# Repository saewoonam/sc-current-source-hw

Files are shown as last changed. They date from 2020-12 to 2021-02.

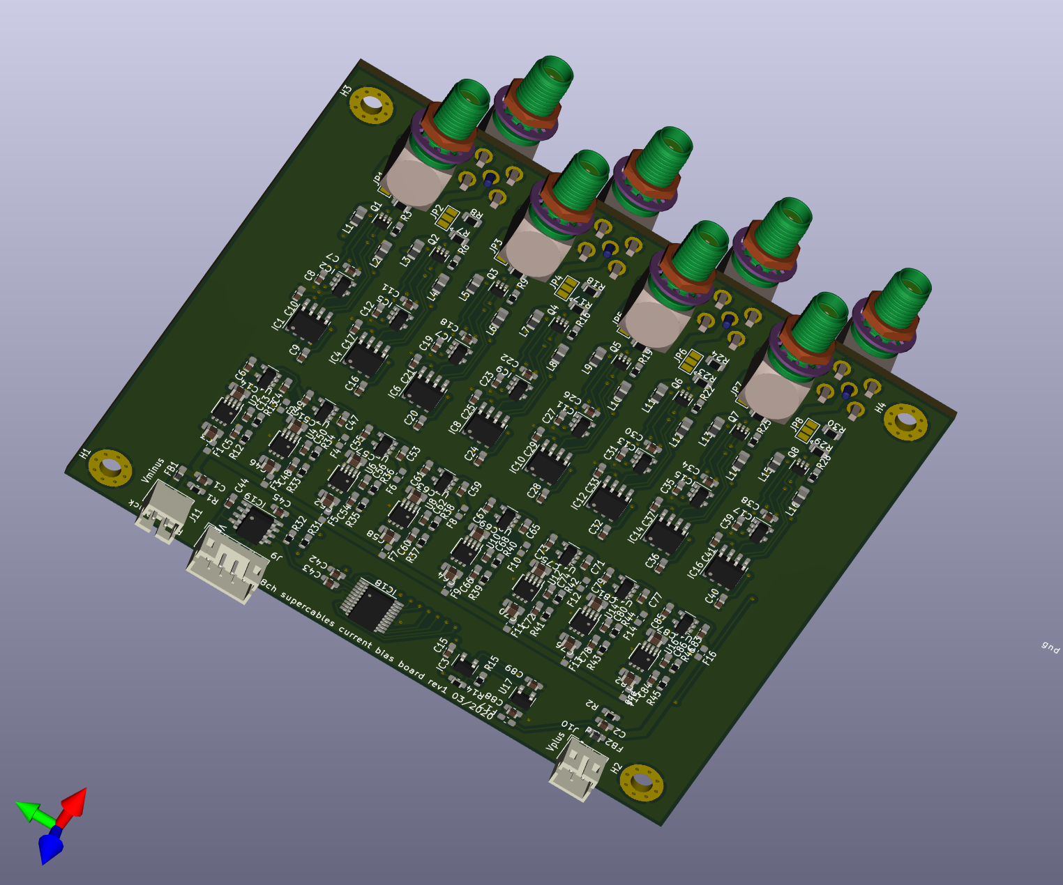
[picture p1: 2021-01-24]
8ch_v5_nosma/8ch_v5_nosma.png

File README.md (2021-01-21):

# CAD file for supercables 8 channel current source

## Folder descriptions:
- 8ch_currentsource_jlc_v4:   KiCAD files of the elecronic circuit
- front_panel:  PCB design for the front panel of the enclosure
- back_panel:  PCB design for rthe back panel of the enclosure
- supercables-curernt-source-enclosure:  FreeCAD file and step files of the assembled box

## [Assembly Instructions](https://github.com/saewoonam/sc-current-source-hw/blob/main/Assembly_Instructions.md)

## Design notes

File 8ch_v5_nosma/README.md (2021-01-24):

# 8ch_currentsource_jlc_v3
Second attempt to make an 8 channel current bias board.  
#  Change from v2
- Added a voltage regulator for each channel

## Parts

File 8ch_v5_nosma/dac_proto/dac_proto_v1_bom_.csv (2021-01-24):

References | Value | Footprint | SPN | SPR
C2 C4 C5 C8 | 0.1uF 50V X7R 0603 | C_0603_1608Metric_Pad1.05x0.95mm_HandSolder | C14663 | LCSC
C6 C7 C9 | 1.0uF 25V X7R 0603 | C_0603_1608Metric_Pad1.05x0.95mm_HandSolder | C29936 | LCSC
C1 C3 | NFM21PS106B0J3D | NFM21PS106B0J3D_v2 | C118986 | LCSC
FB1 | MPZ2012S102AT000 | 805 | C76817 | LCSC
IC1 | AD5675RBRUZ | TSSOP-20_4.4x6.5mm_P0.65mm
IC2 | ISO1541DR | SOIC-8_3.9x4.9mm_P1.27mm | C143028 | LCSC
J1 | Conn_01x04_MountingPin | JST_PH_S4B-PH-SM4-TB_1x04-1MP_P2.00mm_Horizontal
J2 | Conn_01x10_Male | PinHeader_1x10_P2.54mm_Vertical | C89120 | LCSC
J3 | Phoenix 1711725 | TerminalBlock_Phoenix_MKDS-3-2-5.08_1x02_P5.08mm_Horizontal | - | -
JP1 JP2 JP3 JP4 | SolderJumper_2_Open | SolderJumper-2_P1.3mm_Open_RoundedPad1.0x1.5mm
R1 | 2 | R_0603_1608Metric_Pad1.05x0.95mm_HandSolder | C22977 | LCSC
U1 | LP5907MFX-3.3 | SOT-23-5 | C80670 | LCSC

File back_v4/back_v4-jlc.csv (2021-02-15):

Comment | Designator | MPN | LCSC
BAT60B | D1, | BAT60B | C514095
LED | D2, | KT-0603R | C2286
MountingHole | H1,
JST-PH2 | J1, | B2B-PH-SM4-TB(lf)(sn)
JST-SH | J2, J5, | JST-SH-BM04B-SRSS-TB
191-009-113L551 | J3, | 191-009-113L551
STEMMA JST-PH connector | J4, | B4B-PH-SM4-TB(lf)(sn)
10K | R1, R2, | 0603WAF1002T5E | C25804
2K | R3, | 0603WAF2001T5E | C22975
3.3K | R4, | 0603WAF3301T5E | C22978
1K | R5, | 0603WAF1001T5E | C21190
QT_PY | U1, | -
AQY212 | U2, | AQY212GSZ | C129283

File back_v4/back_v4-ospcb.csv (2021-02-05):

Designator | MPN | Quantity | Description
D1, | BAT60AE6327 | 1 | BAT60A
H1, |  | 1 | MountingHole
J1, | B2B-PH-SM4-TB(lf)(sn) | 1 | JST-PH2
J2, J5, | JST-SH-BM04B-SRSS-TB | 2 | JST-SH
J3, | 191-009-113L551 | 1 | 191-009-113L551
J4, | B4B-PH-SM4-TB(lf)(sn) | 1 | STEMMA JST-PH connector
R1, R2, | 0603WAF1002T5E | 2 | 10K
R3, R5, | 0603WAF2001T5E | 2 | 2K
R4, | 0603WAF3301T5E | 1 | 3.3K
U1, | - | 1 | QT_PY
U2, | AQY212GSZ | 1 | AQY212

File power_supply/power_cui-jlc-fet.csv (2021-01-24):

Comment | Designator | MPN | LCSC
4.7uF | C1, | CL32B475KBUYNNE | C29823
10uF | C2, C3, C8, | EMK325B7106KN-T | C13585
330uF 35V | C4, | VE-331M1VTR-1010S | C134522
CP | C5, C6, | DB-5R5D155T
100uF | C7, | CL32A107MQVNNNE | C49066
390pF | C9, C10, |  | C84719
BAT60A | D1, D2, D3, D4, D5, D6, D7, | BAT60AE6327 | C117485
JK-NSMD050-13.2V | F1, | JK-NSMD050-13.2V | C369159
ACM9070-701-2PL-TL01 | FL1, FL2, | ACM9070-701-2PL-TL01 | C14594
Bnx029-01 | FL4, FL5, | Bnx029-01L | C124739
Barrel_Jack_Switch | J1, | PJ-066A
Conn_01x02 | J2, J3, J4, J5, J6, J7, | B2B-PH-K-S(LF)(SN)
SolderJumper_2_Open | JP1, JP2, JP3, JP4, | -
4.7uH | L1, | SDET25201T-4R7MS | C520141
22uH | L2, |  | C207843
NUD3105LT1G | Q1, Q2, | NUD3105LT1G | C14894
BSS84 | Q3, |  | C8492
ZVN4525G | Q4, |  | C154905
ZXP2106G | Q5, |  | C460270
10K | R1, R3, R7, | 0603WAF1002T5E | C25804
1K | R2, R6, | 0603WAF1001T5E | C21190
750 | R4, R5, | 0603WAF7500T5E | C23241
S20K30 | RV1, | S20K30
PDQE10-Q24-D5-D | U1, | PDQE10-Q24-D5-D
AQY212GSZ | U2, U3, | AQY212GSZ | C129283
CRE1S1205SC | U4,

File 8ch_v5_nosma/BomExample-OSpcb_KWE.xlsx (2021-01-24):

Designator | MPN | Qty | Description
C1, C2, C4, C6, C47, C49, C53, C55, C59, C61, C65, C67, C71, C73, C77, C79, C83, C85, C88, C89, | CL10B105KA8NNNC | 20 | 1uF
C3, C14, C46, C51, C52, C57, C58, C63, C64, C69, C70, C75, C76, C81, C82, C87, | CL31B106KBHNNNE | 16 | 10uF X5R 0805
C5, C13, C48, C50, C54, C56, C60, C62, C66, C68, C72, C74, C78, C80, C84, C86, | 0603B103K500NT | 16 | 10nF 50V X7R 0603
C7, C8, C9, C10, C11, C12, C15, C16, C17, C18, C19, C20, C21, C22, C23, C24, C25, C26, C27, C28, C29, C30, C31, C32, C33, C34, C35, C36, C37, C38, C39, C40, C41, C42, C43, C44, C45, | CC0603KPX7R7BB104 | 37 | 100nF
F1, F2, F3, F4, F5, F6, F7, F8, F9, F10, F11, F12, F13, F14, F15, F16, F17, | TLC-FSMD020 | 17 | Polyfuse
FB1, FB2, | BLM18PG181SN1D | 2 | BLM18PG181SN1D
H1, H2, H3, H4, | DNI | 4 | MountingHole_Pad
IC1, IC4, IC6, IC8, IC10, IC12, IC14, IC16, | AD8276ARMZ | 8 | AD8276
IC2, IC3, IC5, IC7, IC9, IC11, IC13, IC15, IC17, | OPA376AIDBVR | 9 | OPA376xxDBVR
IC18, | AD5675RBRUZ | 1 | AD5675RBRUZ
IC19, | ISO1541DR | 1 | ISO1541DR
J1, J2, J3, J4, J5, J6, J7, J8, | SMA-KWE20 | 8 | Conn_Coaxial
J9, | B4B-PH-K-S(LF)(SN) | 1 | B4B-PH-K
J10, J11, | B2B-PH-K-S(LF)(SN) | 2 | JST B2B-PH-K
JP1, JP2, JP3, JP4, JP5, JP6, JP7, JP8, | DNI | 8 | SolderJumper_3_Open
L1, L2, L3, L4, L5, L6, L7, L8, L9, L10, L11, L12, L13, L14, L15, L16, | MMZ2012Y152BTD25 | 16 | MMZ2012Y152B
Q1, Q2, Q3, Q4, Q5, Q6, Q7, Q8, | MMDT3946-7-F | 8 | MMDT3946-7-F
R1, R2, | RC0603FR-072RL | 2 | 2
R3, R6, R9, R14, R15, R16, R19, R22, R25, R28, | RC0603FR-071KL | 10 | 1k
R4, R7, R10, R17, R20, R23, R26, R29, | 2-1625868-7 | 8 | 10 0.1%
R5, R8, R11, R18, R21, R24, R27, R30, | ERA-6AEB102V | 8 | 1k 0.1%
R12, R33, R35, R37, R39, R41, R43, R45, | 0603WAF2002T5E | 8 | 20K
R13, R34, R36, R38, R40, R42, R44, R46, | 0603WAF3572T5E | 8 | 35.7K
R31, R32, | 0603WAF1002T5E | 2 | 10K
U1, U3, U5, U7, U9, U11, U13, U15, U17, | LP5907MFX-3.3 | 9 | LP5907MFX-3.3
U2, U4, U6, U8, U10, U12, U14, U16, | TPS7A3001DGNR | 8 | TPS7A3001

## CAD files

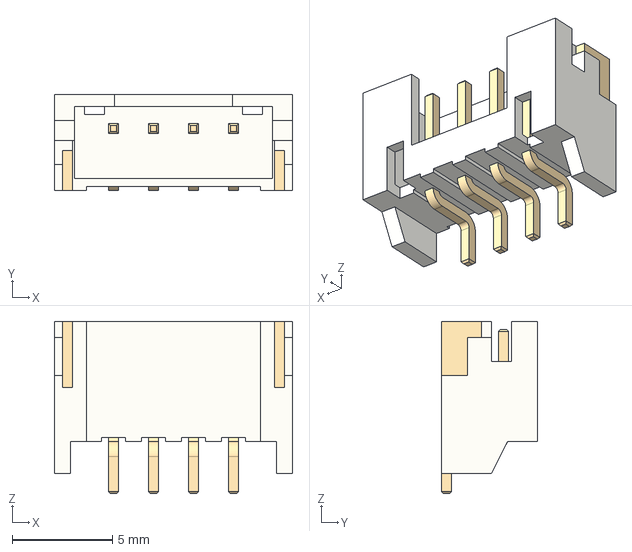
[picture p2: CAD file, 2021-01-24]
8ch_v5_nosma/3D/S4B-PH-SM4-TB.stp
11.9 x 4.80 x 8.60 mm

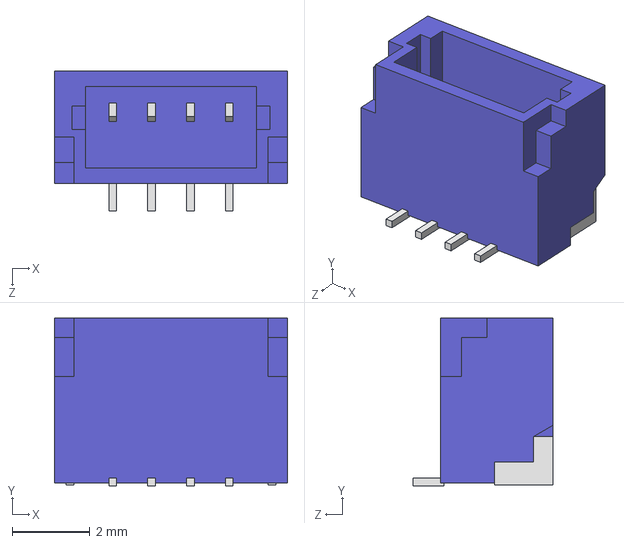
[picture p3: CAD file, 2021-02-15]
back_v4/3D/BM04B-SRSS-TB.STEP
6.00 x 4.32 x 3.60 mm

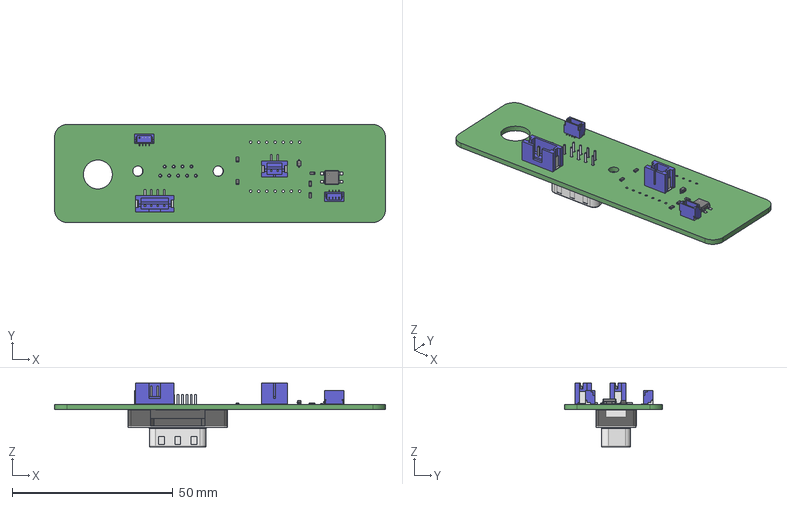
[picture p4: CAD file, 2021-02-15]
back_v4/back_v4.step
103.0 x 30.5 x 19.9 mm

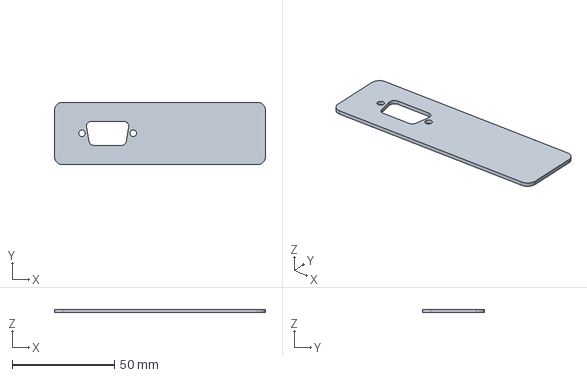
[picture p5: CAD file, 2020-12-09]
front_panel/back_panel.step
103.0 x 30.5 x 1.60 mm

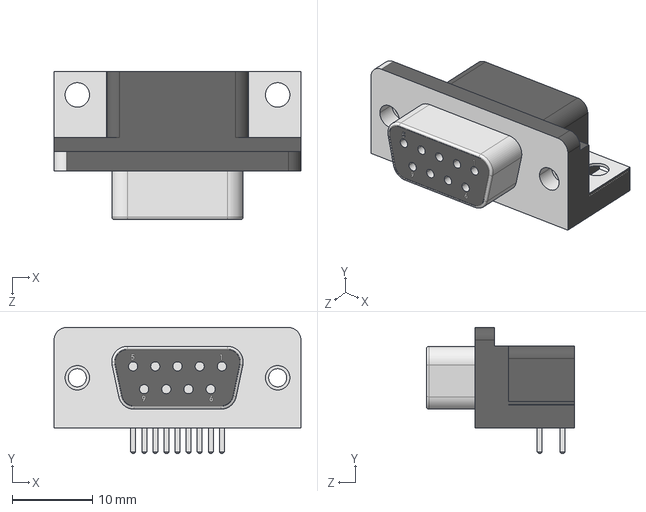
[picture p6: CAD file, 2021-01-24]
power_supply/3D/182-009-213.STEP
30.8 x 15.7 x 18.5 mm

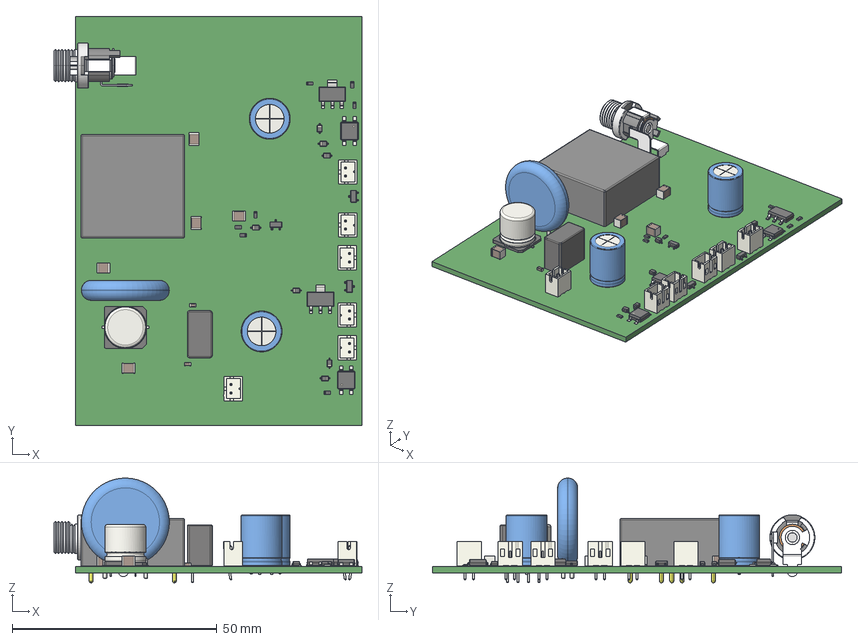
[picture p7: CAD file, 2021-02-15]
power_supply/power_cui.step
75.2 x 100.0 x 25.6 mm

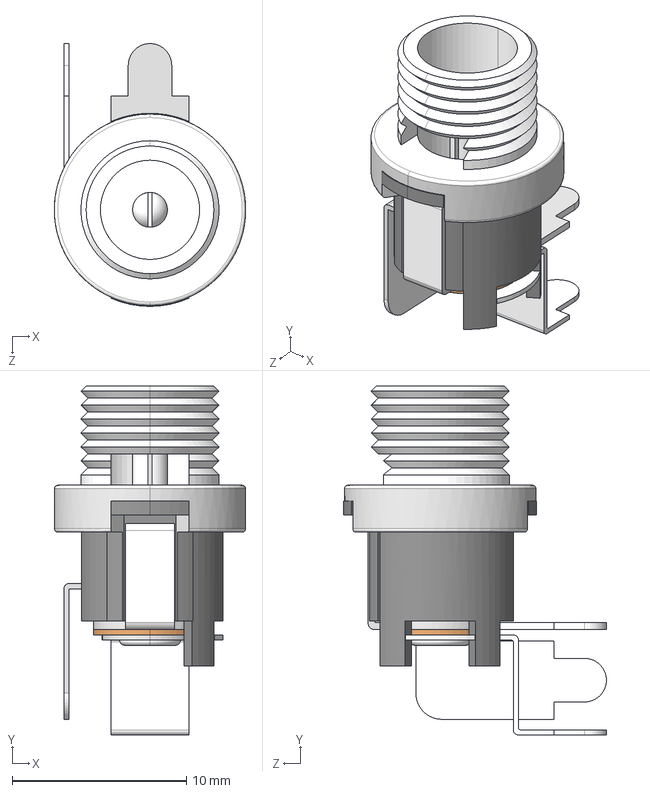
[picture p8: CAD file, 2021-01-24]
supercap/3D/CUI_DEVICES_PJ-066A.step
11.0 x 20.1 x 15.1 mm

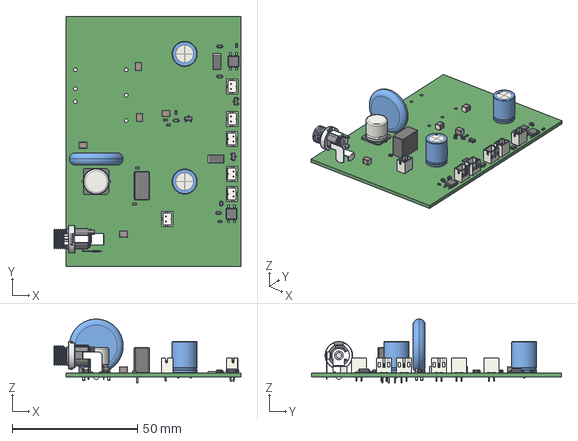
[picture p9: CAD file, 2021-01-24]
supercap/supercap.step
74.7 x 100.0 x 25.5 mm

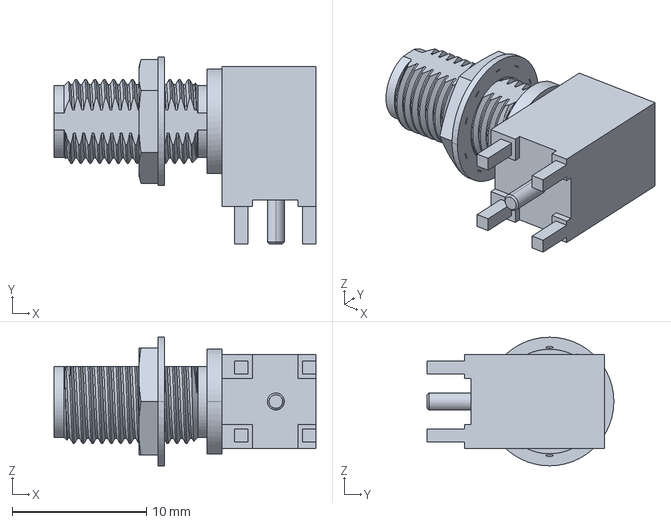
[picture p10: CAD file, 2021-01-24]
8ch_v5_nosma/3D/molex_732512201.stp
19.5 x 13.9 x 9.60 mm

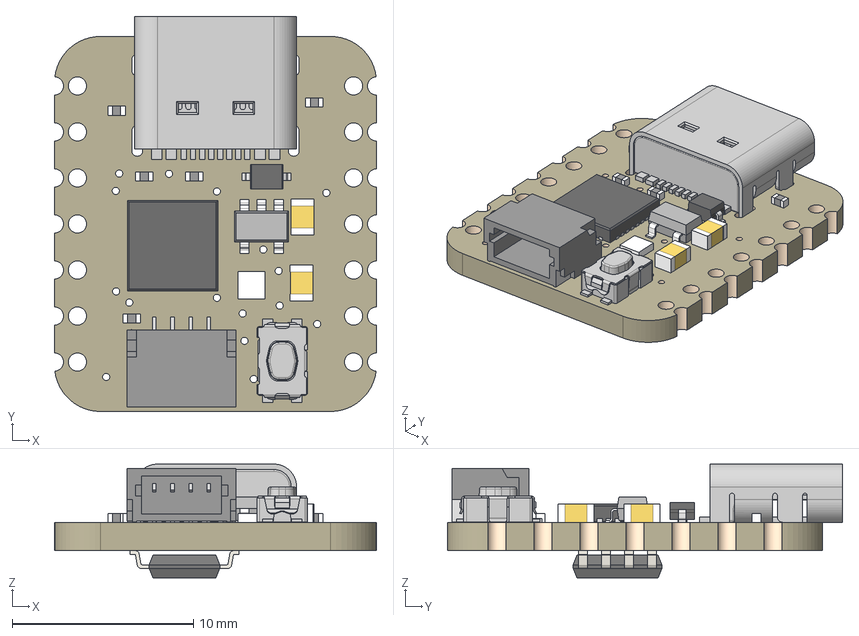
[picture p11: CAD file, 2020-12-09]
back_v4/3D/4600 QTPy.step
17.8 x 21.8 x 6.28 mm
Board
10uF x 2
reset
ATSAMD21E
TPB1,27
5.1K x 5
USB TYPE C
STEMMA_I2C_QTSKINNY
AP2112K-3.3
WS2812B_SK6805_1515
NSR0320
SOIC8_150MIL

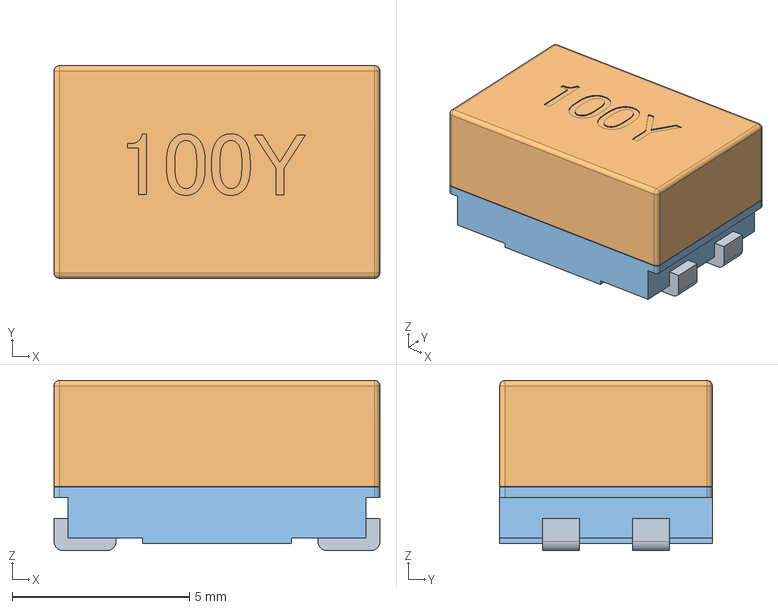
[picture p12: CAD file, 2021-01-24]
power_supply/3D/srf0905-100y.stp
9.20 x 6.00 x 4.80 mm

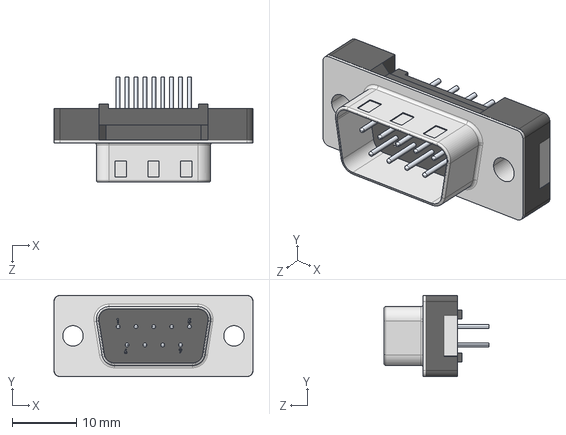
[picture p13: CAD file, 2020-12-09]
back_v4/3D/191-009-113.STEP
30.9 x 12.6 x 16.3 mm

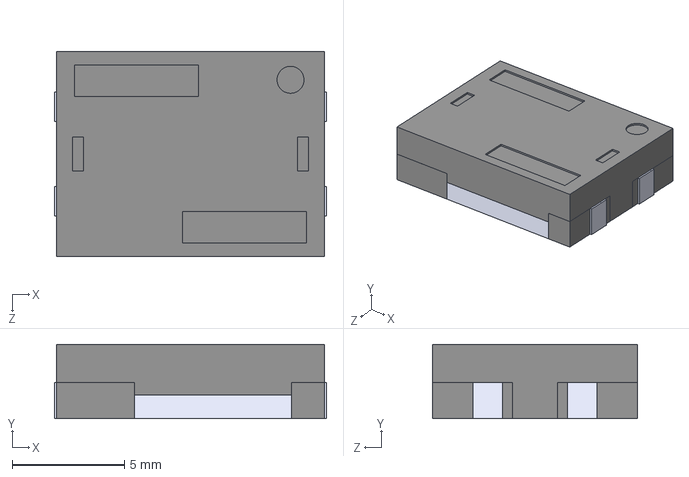
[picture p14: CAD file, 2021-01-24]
power_supply/3D/BNX022-01L.STEP
12.1 x 3.30 x 9.10 mm

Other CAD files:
back_v3/back_v3.step
back_v4/3D/B4B-PH-SM4-TB.STEP

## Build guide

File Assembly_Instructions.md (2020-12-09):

# Ideal assembly instructions
## Parts list for one enclosure
- 8 channel current source circuit board
- front panel PCB with cutouts for SMA connectors
- back panel PCB
- [Hammand 1445L1201 enclosure enclosure](https://www.hawkusa.com/manufacturers/hammond-mfg/enclosures/box-metal/1455l1201?utm_source=octopart&utm_medium=cpc)
- [JST-PH 2 pin power jumper cables](https://www.adafruit.com/product/4714)
- [i2c JST-PH 4 jumper / STEMMA cable](https://www.adafruit.com/product/3568)
- [QT-py adafruit microcontroller](https://www.adafruit.com/product/4600)
- DB9 female pigtail

## Assembly instructions
1.  attach 2 power cable jumpers, one for positive, one for negative voltages to the 8 channel PCB
1.  attach the JST-PH 4 stemma cable to the 8 channel PCB
1.  Remove the metal front and metal back panels from the Hammond enclosure
1.  Slide the printed 8 channel  PCB into hammond enclosure.   Use the middle set of PCB card guides
1.  Attach the front panel PCB to the hammond enclosure.   
1.  Slide the SMA connectors from the 8 channel PCB board through the front panel mounting holes for the SMA connectors.
1.  Use the lock washer and nut to attach each SMA to the front panel PCB
1.  Solder the Adafruit QT PY to the back panel
1.  Connect the power jumper cables and the JST-PH 4 Stemma cable to the back panel
1.  Feed cables into the box and attach back panel to the box
1.  Attach right angle USB-C adapter to the QT-PY board
1.  Attach DB9 pigtail to the backpanel DB9 connector
1.  Apply power to DB9 cable  **Need wirinig details**

## Assembly instructions for backpanel
### Parts list
- 1 Unpopulated back panel PCB
- 2 B2B-PH-SM4-TB  JST-PH 2 pin connector
- 1 B4B-PH-SM4-TB  JST-PH 4 pin connector
- 1 NorComp  191-009-113L551  DB9 male connector
- QT-PY Adafruit microcontroller
### Instructions
1.  Solder JST connectors to one side of the board
2.  Solder DB9 and QT-PY microcontroller to the board on the other side

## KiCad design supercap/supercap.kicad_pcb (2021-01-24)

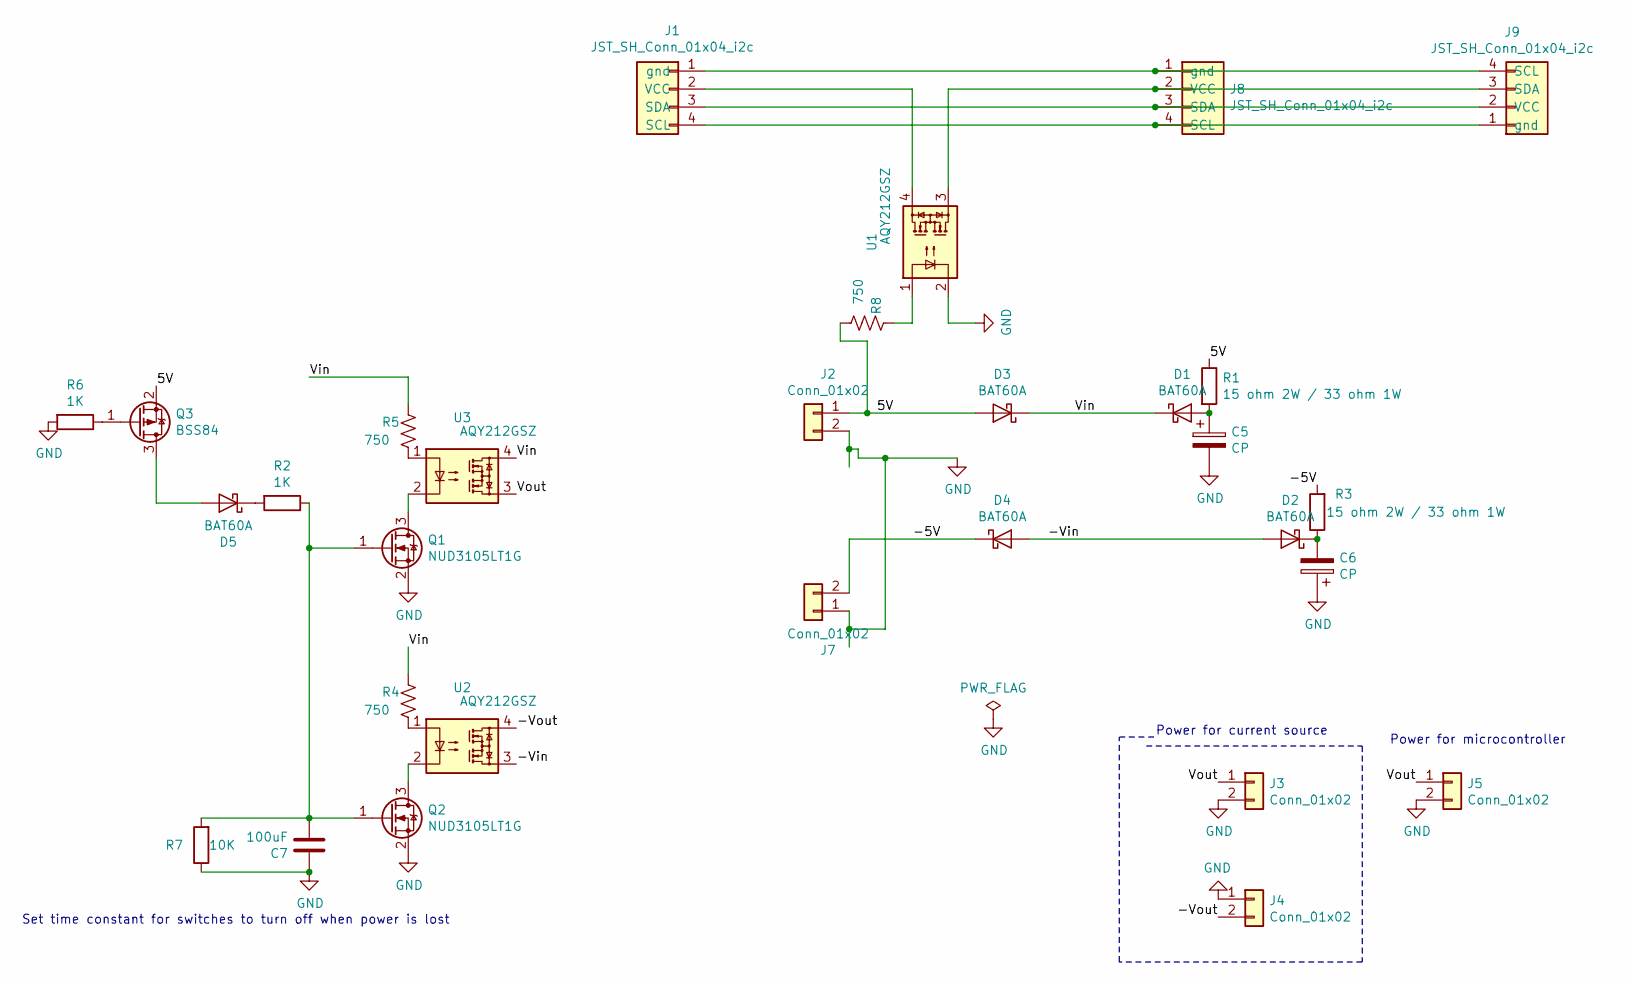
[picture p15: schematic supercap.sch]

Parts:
C5, C6: CP; C_Radial_D21.5mm_H8mm_P5.00mm; MPN DB-5R5D155T
C7: 100uF; C_1210_3225Metric_Pad1.42x2.65mm_HandSolder; MPN CL32A107MQVNNNE; LCSC C49066
D1, D2, D3, D4: BAT60A; D_SOD-323; MPN BAT60AE6327
D5: BAT60A; D_SOD-323; MPN BAT60AE6327; LCSC C117485
J1, J8, J9: JST_SH_Conn_01x04_i2c; JST_SH_BM04B-SRSS-TB_1x04-1MP_P1.00mm_Vertical
J2, J3, J4, J5, J7: Conn_01x02; JST_PH_B2B-PH-K_1x02_P2.00mm_Vertical; MPN B2B-PH-K-S(LF)(SN)
Q1, Q2: NUD3105LT1G; SOT-23; MPN NUD3105LT1G; LCSC C14894
Q3: BSS84; SOT-23; LCSC C8492
R1, R3: 15 ohm 2W / 33 ohm 1W; R_2512_6332Metric_Pad1.52x3.35mm_HandSolder; MPN CRM2512-FX-15R0ELF; LCSC C53728
R2, R6: 1K; R_0603_1608Metric_Pad1.05x0.95mm_HandSolder; MPN 0603WAF1001T5E; LCSC C21190
R4, R5, R8: 750; R_0603_1608Metric_Pad1.05x0.95mm_HandSolder; MPN 0603WAF7500T5E; LCSC C23241
R7: 10K; R_0603_1608Metric_Pad1.05x0.95mm_HandSolder; MPN 0603WAF1002T5E; LCSC C25804
U1, U2, U3: AQY212GSZ; SO-4_4.4x4.3mm_P2.54mm; MPN AQY212GSZ; LCSC C129283

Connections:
/5V: D3.2 (A), J2.1, Q3.2 (S), R1.1, R8.2
/-5V: D4.1 (K), J7.2, R3.2
/-Vin: D2.2 (A), D4.2 (A), U2.3
/-Vout: J4.2, U2.4
/Vin: D1.1 (K), D3.1 (K), R4.1, R5.1, U3.4
/Vout: J3.1, J5.1, U3.3
GND: C5.2, C6.1, C7.1, J2.2, J3.2, J4.1, J5.2, J7.1, Q1.2 (S), Q2.2 (S), R6.2, R7.1, U1.2
unnamed: C5.1, D1.2 (A), R1.2
unnamed: C6.2, D2.1 (K), R3.1
unnamed: C7.2, Q1.1 (G), Q2.1 (G), R2.1, R7.2
unnamed: D5.1 (K), R2.2
unnamed: D5.2 (A), Q3.3 (D)
unnamed: J1.1 (gnd), J8.1 (gnd), J9.4 (SCL)
unnamed: J1.2 (VCC), U1.4
unnamed: J1.3 (SDA), J8.3 (SDA), J9.2 (VCC)
unnamed: J1.4 (SCL), J8.4 (SCL), J9.1 (gnd)
unnamed: J8.2 (VCC), J9.3 (SDA), U1.3
unnamed: Q1.3 (D), U3.2
unnamed: Q2.3 (D), U2.2
unnamed: Q3.1 (G), R6.1
unnamed: R4.2, U2.1
unnamed: R5.2, U3.1
unnamed: R8.1, U1.1

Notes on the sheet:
Power for current source
Power for microcontroller
Set time constant for switches to turn off when power is lost

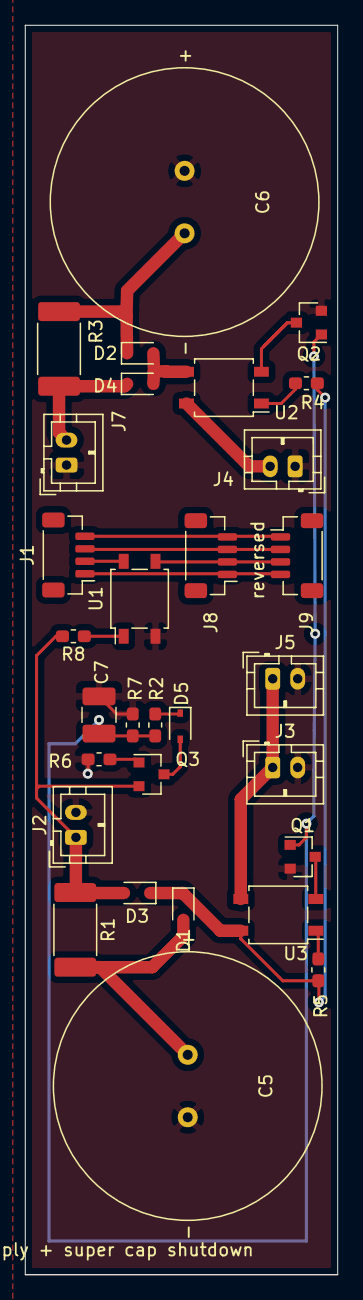
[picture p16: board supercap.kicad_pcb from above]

Board: 2 copper layers, 25.0 x 100.0 mm, 30 parts (0 on the bottom side), 23 nets.

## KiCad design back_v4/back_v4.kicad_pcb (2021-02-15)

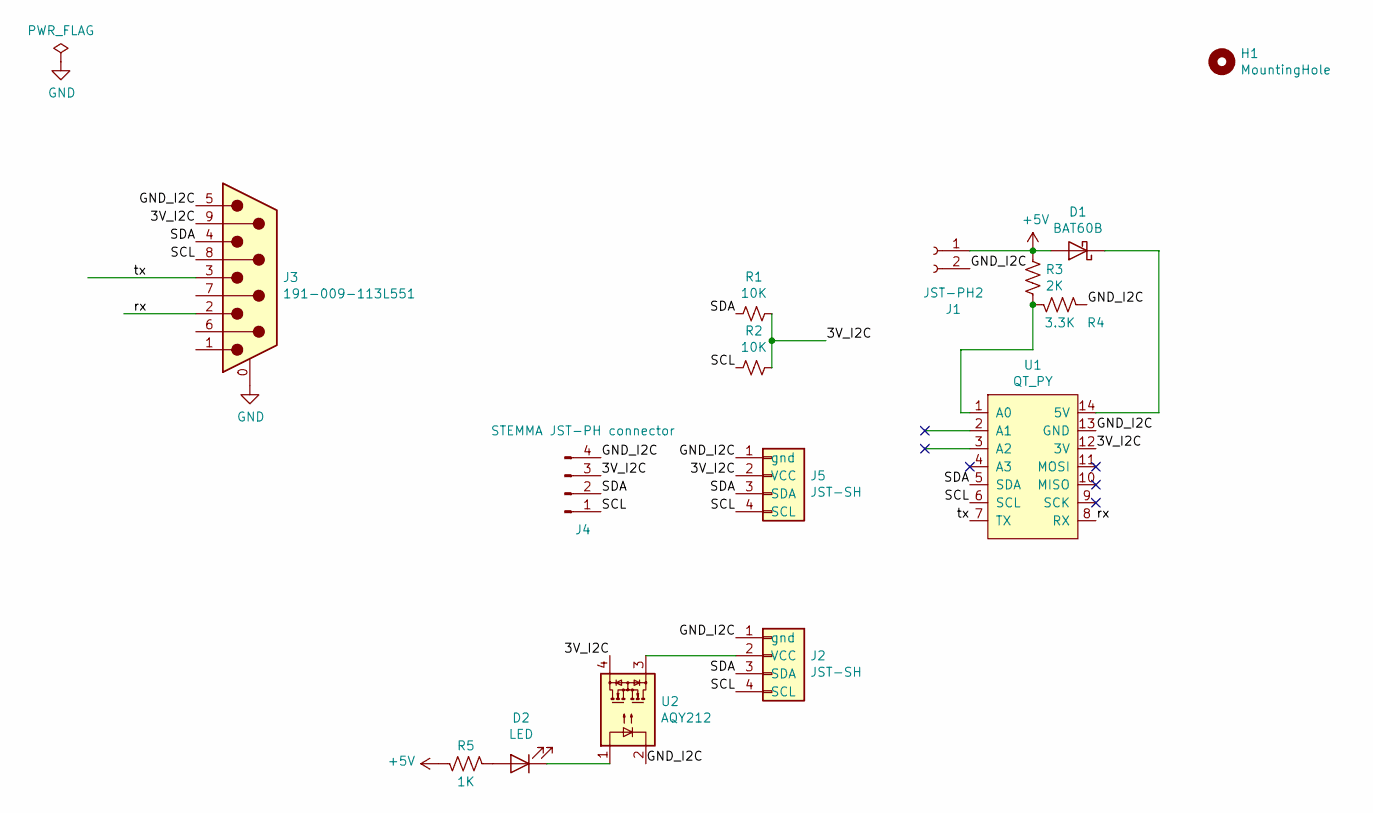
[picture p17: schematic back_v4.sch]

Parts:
D1: BAT60B; D_SOD-323; MPN BAT60B; LCSC C514095
D2: LED; LED_0603_1608Metric_Pad1.05x0.95mm_HandSolder; MPN KT-0603R; LCSC C2286
H1: MountingHole; MountingHole_8.4mm_PJ-066
J1: JST-PH2; JST_PH_B2B-PH-SM4-TB_1x02-1MP_P2.00mm_Vertical; MPN B2B-PH-SM4-TB(lf)(sn)
J2, J5: JST-SH; JST_SH_BM04B-SRSS-TB_1x04-1MP_P1.00mm_Vertical; MPN JST-SH-BM04B-SRSS-TB
J3: 191-009-113L551; DSUB-9_Male_Vertical_P2.77x2.84mm_MountingHoles; MPN 191-009-113L551
J4: STEMMA JST-PH connector; JST_PH_B4B-PH-SM4-TB_1x04-1MP_P2.00mm_Vertical; MPN B4B-PH-SM4-TB(lf)(sn)
R1: 10K; R_0603_1608Metric_Pad1.05x0.95mm_HandSolder; MPN 0603WAF1002T5E
R2: 10K; R_0603_1608Metric_Pad1.05x0.95mm_HandSolder; MPN 0603WAF1002T5E; LCSC C25804
R3: 2K; R_0603_1608Metric_Pad1.05x0.95mm_HandSolder; MPN 0603WAF2001T5E; LCSC C22975
R4: 3.3K; R_0603_1608Metric_Pad1.05x0.95mm_HandSolder; MPN 0603WAF3301T5E; LCSC C22978
R5: 1K; R_0603_1608Metric_Pad1.05x0.95mm_HandSolder; MPN 0603WAF1001T5E; LCSC C21190
U1: QT_PY; QT_PY_DIP-14_600_ELL
U2: AQY212; SO-4_4.4x4.3mm_P2.54mm; MPN AQY212GSZ; LCSC C129283

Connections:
+5V: D1.2 (A), J1.1, R3.1, R5.1
/3V_I2C: J3.9, J4.3, J5.2 (VCC), R1.1, R2.1, U1.12 (3V), U2.4
/GND_I2C: J1.2, J2.1 (gnd), J3.5, J4.4, J5.1 (gnd), R4.2, U1.13 (GND), U2.2
/SCL: J2.4 (SCL), J3.8, J4.1, J5.4 (SCL), R2.2, U1.6 (SCL)
/SDA: J2.3 (SDA), J3.4, J4.2, J5.3 (SDA), R1.2, U1.5 (SDA)
/rx: J3.2, U1.8 (RX)
/tx: J3.3, U1.7 (TX)
GND: J3.0 (PAD)
unnamed: D1.1 (K), U1.14 (5V)
unnamed: D2.1 (K), U2.1
unnamed: D2.2 (A), R5.2
unnamed: J2.2 (VCC), U2.3
unnamed: R3.2, R4.1, U1.1 (A0)

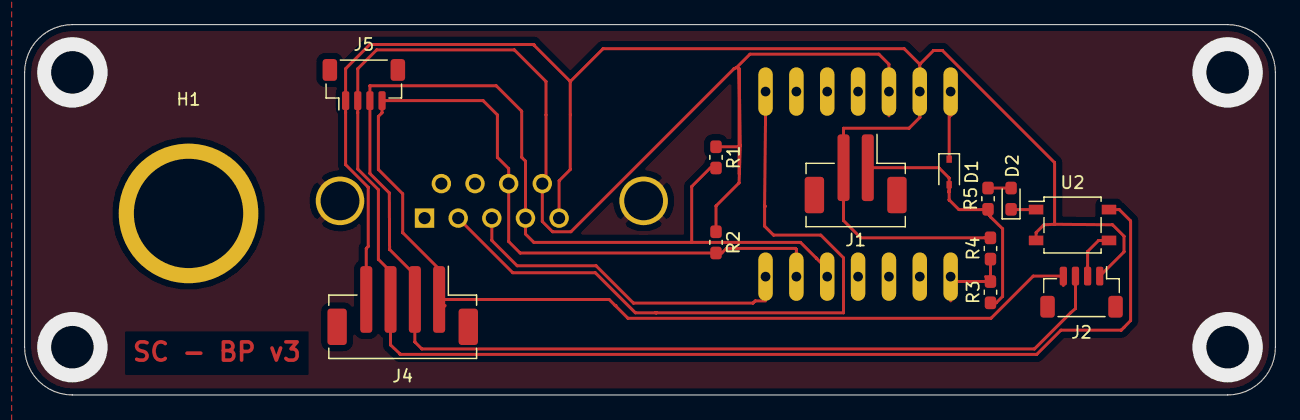
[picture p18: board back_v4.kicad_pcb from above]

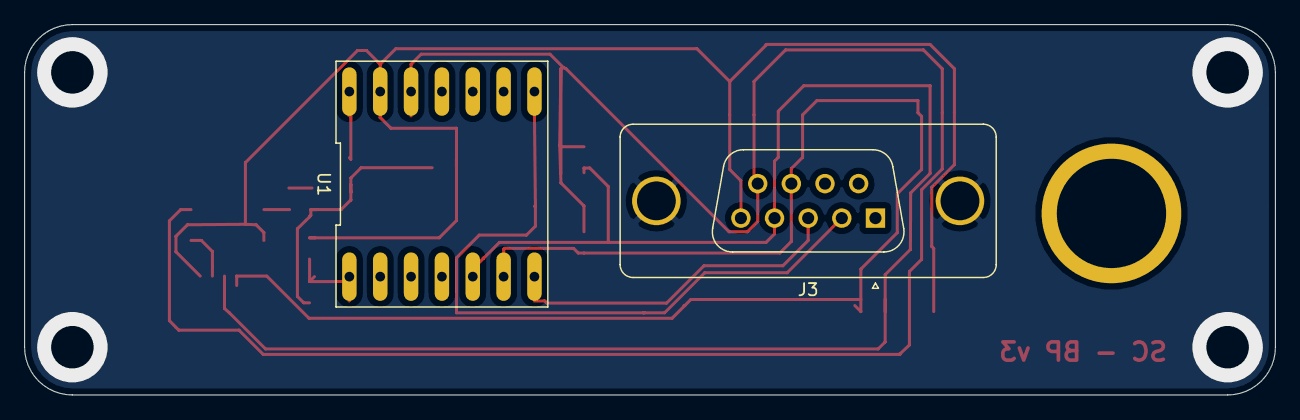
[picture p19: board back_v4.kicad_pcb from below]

Board: 2 copper layers, 103.0 x 30.5 mm, 15 parts (2 on the bottom side), 12 nets.

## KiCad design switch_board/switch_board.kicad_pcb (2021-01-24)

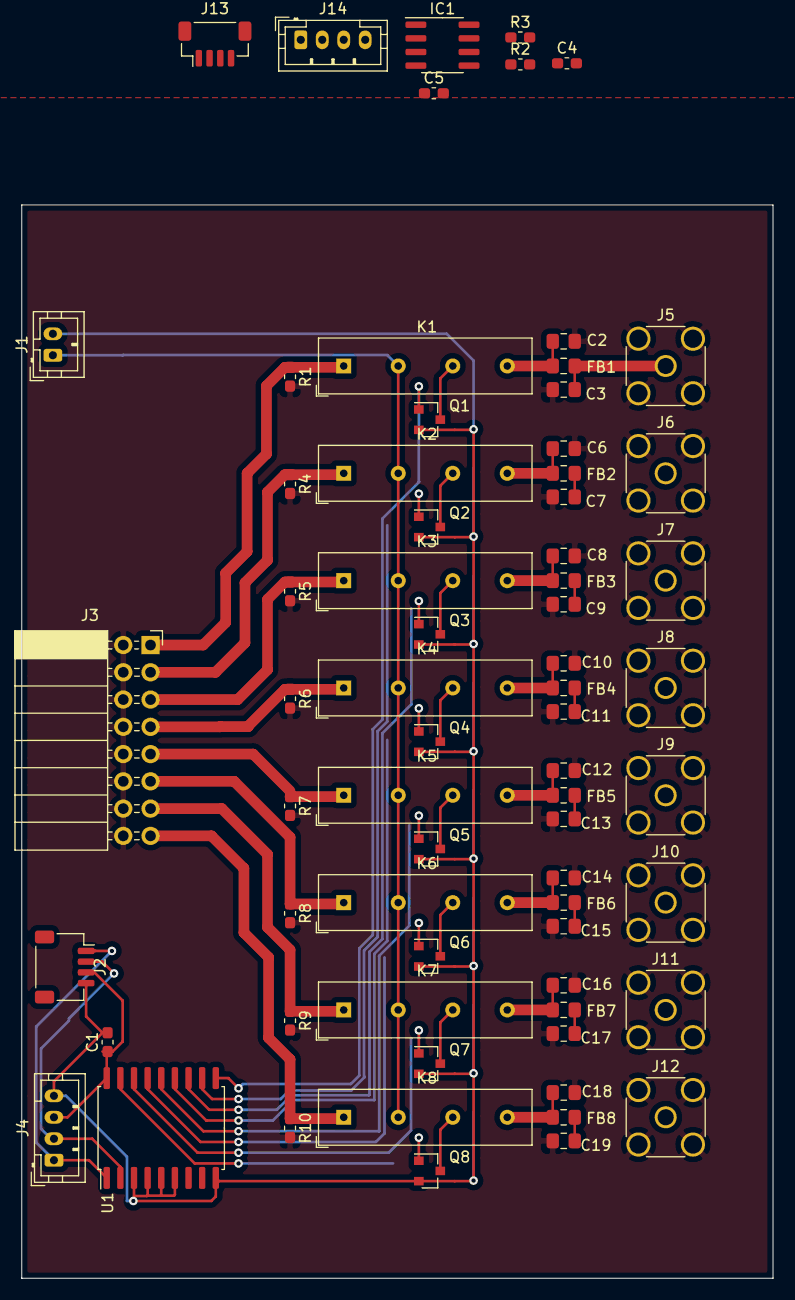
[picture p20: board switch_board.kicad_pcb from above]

Board: 2 copper layers, 70.0 x 100.0 mm, 69 parts (0 on the bottom side), 52 nets.

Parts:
C1, C4, C5: 100nF; C_0603_1608Metric_Pad1.05x0.95mm_HandSolder
C2, C3, C6, C7, C8, C9, C10, C11, C12, C13, C14, C15, C16, C17, C18, C19: 100uF; C_0805_2012Metric_Pad1.15x1.40mm_HandSolder
FB1, FB2, FB3, FB4, FB5, FB6, FB7, FB8: 4.7uH; L_0805_2012Metric_Pad1.15x1.40mm_HandSolder
IC1: ISO1541DR; SOIC-8_3.9x4.9mm_P1.27mm
J1: Conn_01x02; JST_PH_B2B-PH-K_1x02_P2.00mm_Vertical
J2: Conn_01x04_i2c; JST_SH_SM04B-SRSS-TB_1x04-1MP_P1.00mm_Horizontal
J3: Conn_02x08_Odd_Even; PinSocket_2x08_P2.54mm_Horizontal
J4: Conn_01x04_i2c; JST_PH_B4B-PH-K_1x04_P2.00mm_Vertical
J5, J6, J7, J8, J9, J10, J11, J12: Conn_Coaxial; SMA_Amphenol_132134_Vertical
J13: Conn_01x04_i2c; JST_SH_BM04B-SRSS-TB_1x04-1MP_P1.00mm_Vertical
J14: B4B-PH-K; JST_PH_B4B-PH-K_1x04_P2.00mm_Vertical
K1, K2, K3, K4, K5, K6, K7, K8: SILxx-1Axx-71x; Relay_SPST_StandexMeder_SIL_Form1A
Q1, Q2, Q3, Q4, Q5, Q6, Q7, Q8: NUD3105LT1G; SOT-23
R1, R2, R3, R4, R5, R6, R7, R8, R9, R10: 10K; R_0603_1608Metric_Pad1.05x0.95mm_HandSolder
U1: MCP23008-E_SO; SOIC-18W_7.5x11.6mm_P1.27mm

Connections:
+5V: J1.1, K1.3, K2.3, K3.3, K4.3, K5.3, K6.3, K7.3, K8.3
/Sheet601B3DC5/out: C3.1, FB1.1, J5.1
/Sheet601B43CA/Vin: C4.1, IC1.1, J13.3, J14.3
/Sheet601B43CA/Vpower: C5.1, IC1.8, R2.1, R3.1
/Sheet601B43CA/scl: IC1.6, R3.2
/Sheet601B43CA/sda: IC1.7, R2.2
/in0: J3.1, K1.1, R1.1
/in1: J3.3, K2.1, R4.1
/in2: J3.5, K3.1, R5.1
/in3: J3.7, K4.1, R6.1
/in4: J3.9, K5.1, R7.1
/in5: J3.11, K6.1, R8.1
/in6: J3.13, K7.1, R9.1
/in7: J3.15, K8.1, R10.1
/s0: Q1.1, U1.10
/s1: Q2.1, U1.11
/s2: Q3.1, U1.12
/s3: Q4.1, U1.13
/s4: Q5.1, U1.14
/s5: Q6.1, U1.15
/s6: Q7.1, U1.16
/s7: Q8.1, U1.17
/scl: J2.1, J4.1, U1.1
/sda: J2.2, J4.2, U1.2
/sheet601BFE22/out: C7.1, FB2.1, J6.1
/sheet601C077A/out: C17.1, FB7.1, J11.1
/sheet601C077B/out: C19.1, FB8.1, J12.1
/sheet601C0132/out: C9.1, FB3.1, J7.1
/sheet601C0133/out: C11.1, FB4.1, J8.1
/sheet601C0778/out: C13.1, FB5.1, J9.1
/sheet601C0779/out: C15.1, FB6.1, J10.1
GND: C2.2, C3.2, C5.2, C6.2, C7.2, C8.2, C9.2, C10.2, C11.2, C12.2, C13.2, C14.2, C15.2, C16.2, C17.2, C18.2, C19.2, IC1.5, J3.2, J3.4, J3.6, J3.8, J3.10, J3.12, J3.14, J3.16, J5.2, J6.2, J7.2, J8.2, J9.2, J10.2, J11.2, J12.2, R1.2, R4.2, R5.2, R6.2, R7.2, R8.2, R9.2, R10.2
GNDD: C1.2, C4.2, IC1.4, J1.2, J2.4, J4.4, J13.4, J14.4, Q1.2, Q2.2, Q3.2, Q4.2, Q5.2, Q6.2, Q7.2, Q8.2, U1.3, U1.4, U1.5, U1.6, U1.9
unnamed: C2.1, FB1.2, K1.7
unnamed: C6.1, FB2.2, K2.7
unnamed: C8.1, FB3.2, K3.7
unnamed: C10.1, FB4.2, K4.7
unnamed: C12.1, FB5.2, K5.7
unnamed: C14.1, FB6.2, K6.7
unnamed: C16.1, FB7.2, K7.7
unnamed: C18.1, FB8.2, K8.7
unnamed: IC1.2, J13.2, J14.2
unnamed: IC1.3, J13.1, J14.1
unnamed: K1.5, Q1.3
unnamed: K2.5, Q2.3
unnamed: K3.5, Q3.3
unnamed: K4.5, Q4.3
unnamed: K5.5, Q5.3
unnamed: K6.5, Q6.3
unnamed: K7.5, Q7.3
unnamed: K8.5, Q8.3
VCC: C1.1, J2.3, J4.3, U1.18

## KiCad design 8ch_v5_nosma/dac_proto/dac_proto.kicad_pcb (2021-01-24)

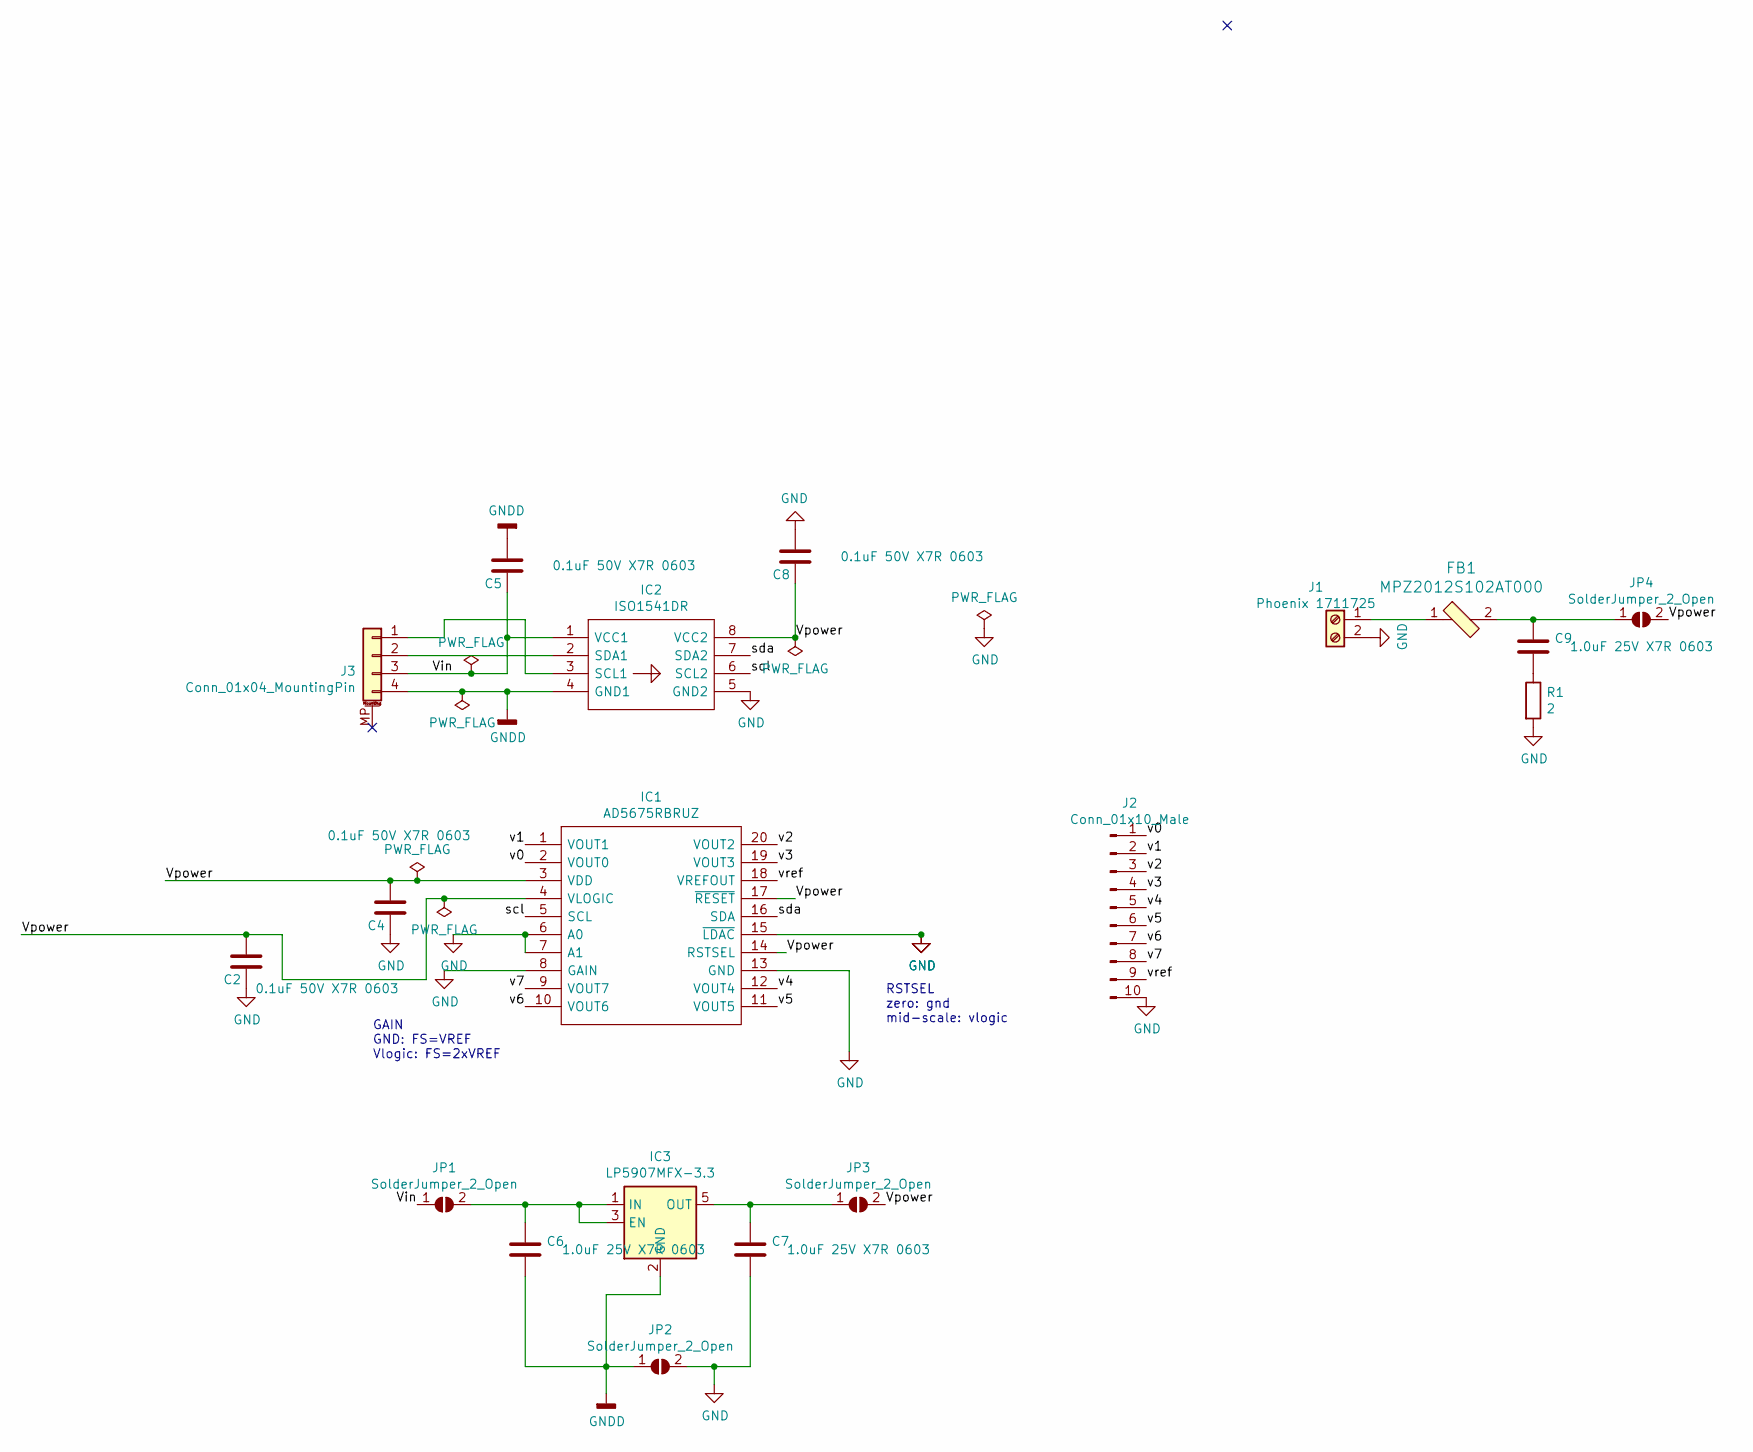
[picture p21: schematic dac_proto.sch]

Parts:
C2, C4, C5, C8: 0.1uF 50V X7R 0603; C_0603_1608Metric_Pad1.05x0.95mm_HandSolder; Part CC0603KRX7R9BB104; Digikey 490-1767-1-ND
C6, C7, C9: 1.0uF 25V X7R 0603; C_0603_1608Metric_Pad1.05x0.95mm_HandSolder; MPN CL10B105KA8NNNC
FB1: MPZ2012S102AT000; 0805; MPN MPZ2012S102AT000; Digi-Key_PN 445-5223-1-ND
IC1: AD5675RBRUZ; TSSOP-20_4.4x6.5mm_P0.65mm; MPN AD5675RBRUZ
IC2: ISO1541DR; SOIC-8_3.9x4.9mm_P1.27mm; MPN ISO1541DR
IC3: LP5907MFX-3.3; SOT-23-5; MPN LP5907MFX-3.3
J1: Phoenix 1711725; TerminalBlock_Phoenix_MKDS-3-2-5.08_1x02_P5.08mm_Horizontal; MPN 1711725
J2: Conn_01x10_Male; PinHeader_1x10_P2.54mm_Vertical
J3: Conn_01x04_MountingPin; JST_PH_S4B-PH-SM4-TB_1x04-1MP_P2.00mm_Horizontal
JP1, JP2, JP3, JP4: SolderJumper_2_Open; SolderJumper-2_P1.3mm_Open_RoundedPad1.0x1.5mm
R1: 2; R_0603_1608Metric_Pad1.05x0.95mm_HandSolder; MPN 0603WAF200KT5E

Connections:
/Vin: C5.1, IC2.1 (VCC1), J3.3, JP1.1 (A)
/Vpower: C2.2, C4.2, C8.1, IC1.3 (VDD), IC1.4 (VLOGIC), IC1.14 (RSTSEL), IC1.17 (~RESET), IC2.8 (VCC2), JP3.2 (B), JP4.2 (B)
/scl: IC1.5 (SCL), IC2.6 (SCL2)
/sda: IC1.16 (SDA), IC2.7 (SDA2)
/v0: IC1.2 (VOUT0), J2.1
/v1: IC1.1 (VOUT1), J2.2
/v2: IC1.20 (VOUT2), J2.3
/v3: IC1.19 (VOUT3), J2.4
/v4: IC1.12 (VOUT4), J2.5
/v5: IC1.11 (VOUT5), J2.6
/v6: IC1.10 (VOUT6), J2.7
/v7: IC1.9 (VOUT7), J2.8
/vref: IC1.18 (VREFOUT), J2.9
GND: C2.1, C4.1, C7.2, C8.2, IC1.6 (A0), IC1.7 (A1), IC1.8 (GAIN), IC1.13 (GND), IC1.15 (~LDAC), IC2.5 (GND2), J1.2, J2.10, JP2.2 (B), R1.2
GNDD: C5.2, C6.2, IC2.4 (GND1), IC3.2 (GND), J3.4, JP2.1 (A)
unnamed: C6.1, IC3.1 (IN), IC3.3 (EN), JP1.2 (B)
unnamed: C7.1, IC3.5 (OUT), JP3.1 (A)
unnamed: C9.1, FB1.2, JP4.1 (A)
unnamed: C9.2, R1.1
unnamed: FB1.1, J1.1
unnamed: IC2.2 (SDA1), J3.2
unnamed: IC2.3 (SCL1), J3.1

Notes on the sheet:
GAIN GND: FS=VREF Vlogic: FS=2xVREF
RSTSEL zero: gnd mid-scale: vlogic

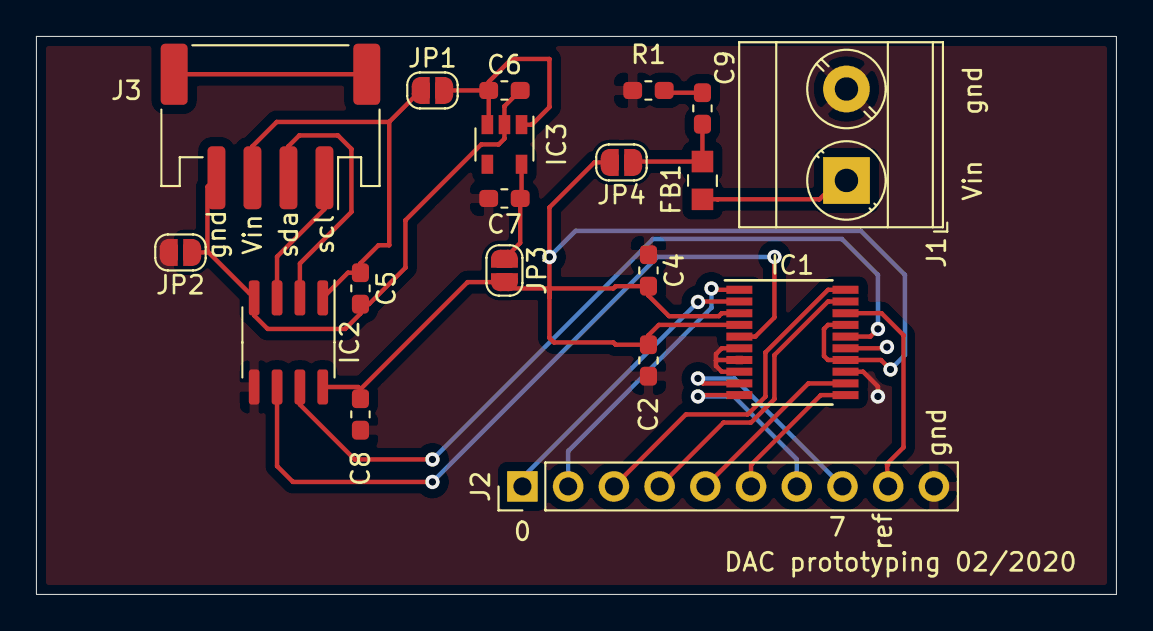
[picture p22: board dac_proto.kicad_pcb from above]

Board: 2 copper layers, 60.0 x 31.0 mm, 19 parts (0 on the bottom side), 22 nets.

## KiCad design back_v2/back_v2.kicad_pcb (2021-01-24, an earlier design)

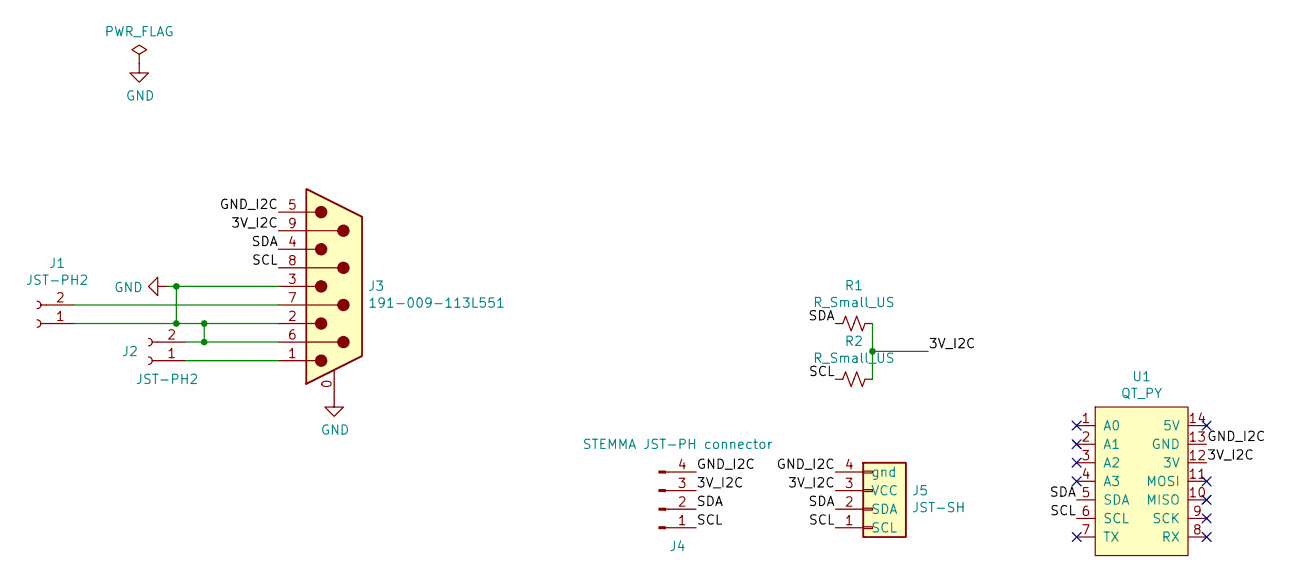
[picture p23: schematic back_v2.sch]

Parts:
J1, J2: JST-PH2; JST_PH_B2B-PH-SM4-TB_1x02-1MP_P2.00mm_Vertical; MPN B2B-PH-SM4-TB(lf)(sn)
J3: 191-009-113L551; DSUB-9_Male_Vertical_P2.77x2.84mm_MountingHoles; MPN 191-009-113L551
J4: STEMMA JST-PH connector; JST_PH_B4B-PH-SM4-TB_1x04-1MP_P2.00mm_Vertical; MPN B4B-PH-SM4-TB(lf)(sn)
J5: JST-SH; JST_SH_BM04B-SRSS-TB_1x04-1MP_P1.00mm_Vertical; MPN JST-SH-BM04B-SRSS-TB
R1, R2: R_Small_US; R_0603_1608Metric_Pad1.05x0.95mm_HandSolder
U1: QT_PY

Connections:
/3V_I2C: J3.9, J4.3, J5.3 (VCC), R1.1, R2.1, U1.12 (3V)
/GND_I2C: J3.5, J4.4, J5.4 (gnd), U1.13 (GND)
/SCL: J3.8, J4.1, J5.1 (SCL), R2.2, U1.6 (SCL)
/SDA: J3.4, J4.2, J5.2 (SDA), R1.2, U1.5 (SDA)
GND: J1.1, J2.2, J3.0 (PAD), J3.2, J3.3, J3.6
unnamed: J1.2, J3.7
unnamed: J2.1, J3.1

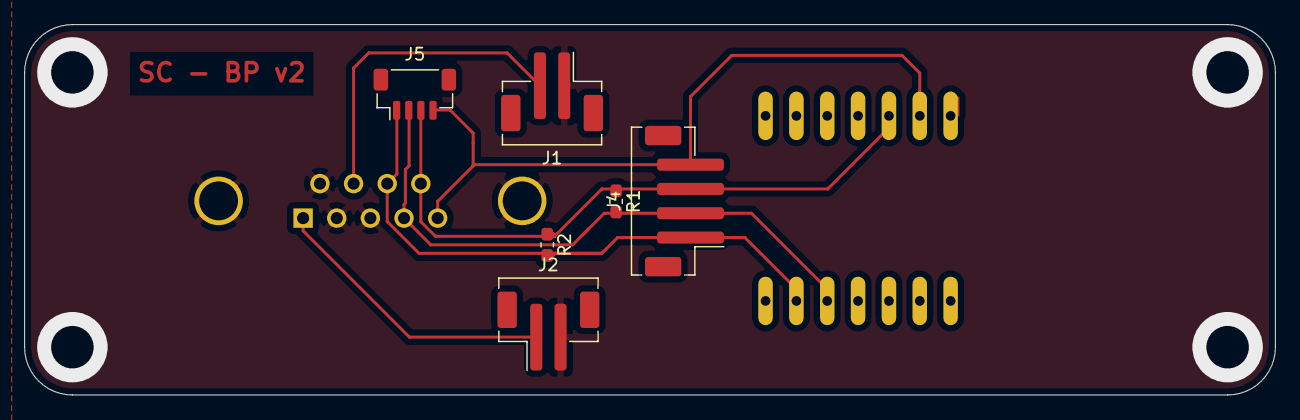
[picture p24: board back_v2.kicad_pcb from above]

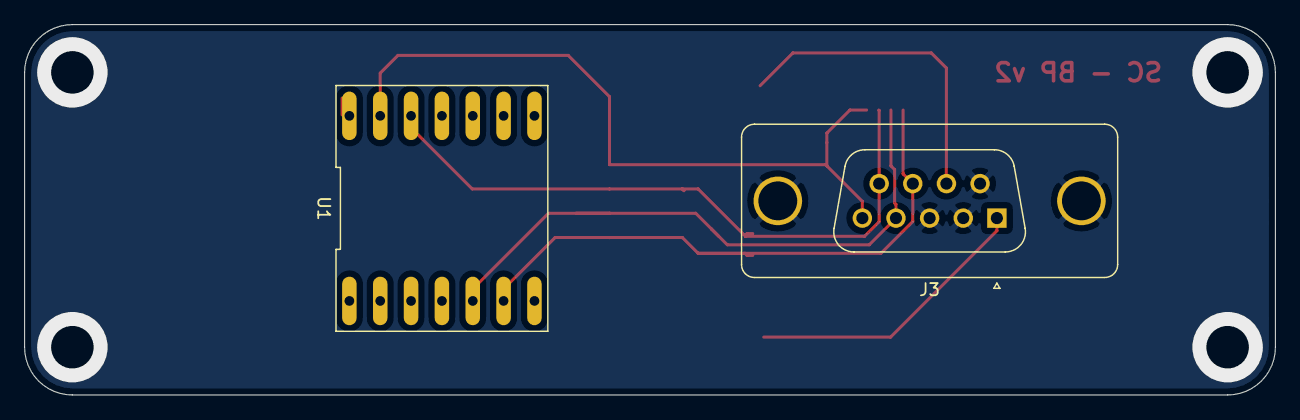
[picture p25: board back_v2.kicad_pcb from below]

Board: 2 copper layers, 103.0 x 30.5 mm, 8 parts (2 on the bottom side), 7 nets.

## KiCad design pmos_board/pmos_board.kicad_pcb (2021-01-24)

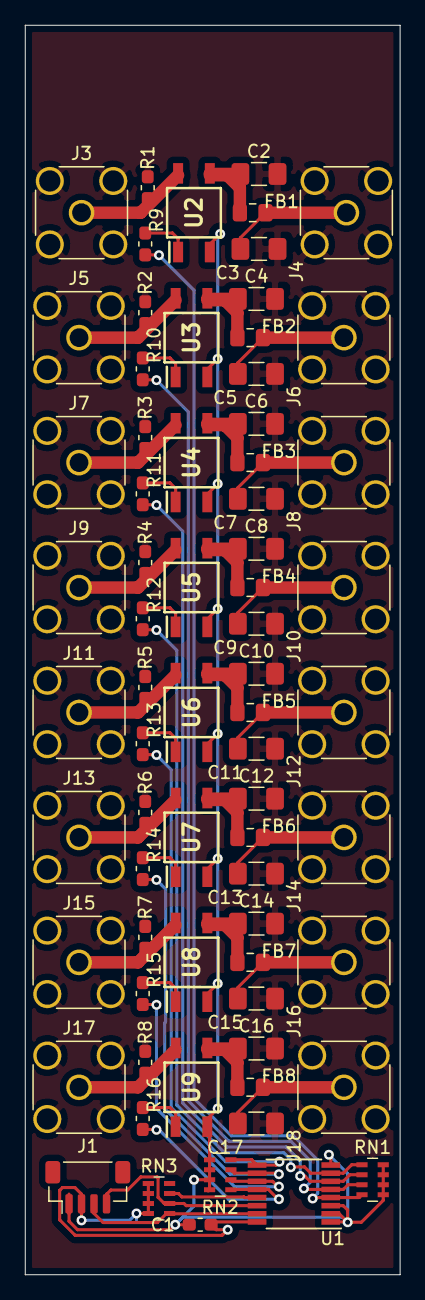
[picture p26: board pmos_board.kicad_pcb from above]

Board: 2 copper layers, 30.0 x 100.0 mm, 70 parts (0 on the bottom side), 46 nets.

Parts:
C1: 100nF; C_0603_1608Metric_Pad1.05x0.95mm_HandSolder
C2, C3, C4, C5, C6, C7, C8, C9, C10, C11, C12, C13, C14, C15, C16, C17: 100uF; C_1206_3216Metric_Pad1.42x1.75mm_HandSolder
FB1, FB2, FB3, FB4, FB5, FB6, FB7, FB8: Ferrite_Bead; L_0805_2012Metric_Pad1.15x1.40mm_HandSolder
J1: Conn_01x04; JST_SH_BM04B-SRSS-TB_1x04-1MP_P1.00mm_Vertical
J3, J4, J5, J6, J7, J8, J9, J10, J11, J12, J13, J14, J15, J16, J17, J18: Conn_Coaxial; SMA_Amphenol_132134_Vertical
R1, R2, R3, R4, R5, R6, R7, R8: 10K 0.1%; R_0603_1608Metric_Pad1.05x0.95mm_HandSolder
R9, R10, R11, R12, R13, R14, R15, R16: 390; R_0603_1608Metric_Pad1.05x0.95mm_HandSolder
RN1, RN2, RN3: 4 x 10K ohm; R_Array_Concave_4x0603
U1: TCA9534APWR; TSSOP-16_4.4x5mm_P0.65mm
U2, U3, U4, U5, U6, U7, U8, U9: AQY212GSZ; AQY211G2S_samacsys

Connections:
+3V3: C1.2, J1.2, RN3.1, RN3.2, RN3.3, RN3.4, U1.16
/scl: J1.4, RN3.6, U1.14
/sda: J1.3, RN3.5, U1.15
/sw1: R9.2, RN1.4, U1.4
/sw2: R10.2, RN1.3, U1.5
/sw3: R11.2, RN1.2, U1.6
/sw4: R12.2, RN1.1, U1.7
/sw5: R13.2, RN2.4, U1.9
/sw6: R14.2, RN2.3, U1.10
/sw7: R15.2, RN2.2, U1.11
/sw8: R16.2, RN2.1, U1.12
GND: C2.2, C3.2, C4.2, C5.2, C6.2, C7.2, C8.2, C9.2, C10.2, C11.2, C12.2, C13.2, C14.2, C15.2, C16.2, C17.2, J3.2, J4.2, J5.2, J6.2, J7.2, J8.2, J9.2, J10.2, J11.2, J12.2, J13.2, J14.2, J15.2, J16.2, J17.2, J18.2, R1.2, R2.2, R3.2, R4.2, R5.2, R6.2, R7.2, R8.2
GNDD: C1.1, J1.1, RN1.5, RN1.6, RN1.7, RN1.8, RN2.5, RN2.6, RN2.7, RN2.8, U1.1, U1.2, U1.3, U1.8, U2.2, U3.2, U4.2, U5.2, U6.2, U7.2, U8.2, U9.2
unnamed: C2.1, FB1.2, U2.3
unnamed: C3.1, FB1.1, J4.1
unnamed: C4.1, FB2.2, U3.3
unnamed: C5.1, FB2.1, J6.1
unnamed: C6.1, FB3.2, U4.3
unnamed: C7.1, FB3.1, J8.1
unnamed: C8.1, FB4.2, U5.3
unnamed: C9.1, FB4.1, J10.1
unnamed: C10.1, FB5.2, U6.3
unnamed: C11.1, FB5.1, J12.1
unnamed: C12.1, FB6.2, U7.3
unnamed: C13.1, FB6.1, J14.1
unnamed: C14.1, FB7.2, U8.3
unnamed: C15.1, FB7.1, J16.1
unnamed: C16.1, FB8.2, U9.3
unnamed: C17.1, FB8.1, J18.1
unnamed: J3.1, R1.1, U2.4
unnamed: J5.1, R2.1, U3.4
unnamed: J7.1, R3.1, U4.4
unnamed: J9.1, R4.1, U5.4
unnamed: J11.1, R5.1, U6.4
unnamed: J13.1, R6.1, U7.4
unnamed: J15.1, R7.1, U8.4
unnamed: J17.1, R8.1, U9.4
unnamed: R9.1, U2.1
unnamed: R10.1, U3.1
unnamed: R11.1, U4.1
unnamed: R12.1, U5.1
unnamed: R13.1, U6.1
unnamed: R14.1, U7.1
unnamed: R15.1, U8.1
unnamed: R16.1, U9.1
unnamed: RN3.7, U1.13

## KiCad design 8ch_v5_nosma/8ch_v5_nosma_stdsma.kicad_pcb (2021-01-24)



Board: 4 copper layers, 90.0 x 98.0 mm, 237 parts (4 on the bottom side), 138 nets.

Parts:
C1, C2, C4, C6, C47, C49, C53, C55, C59, C61, C65, C67, C71, C73, C77, C79, C83, C85, C88, C89: 1uF; C_0603_1608Metric_Pad1.05x0.95mm_HandSolder
C3, C14, C46, C51, C52, C57, C58, C63, C64, C69, C70, C75, C76, C81, C82, C87: 10uF X5R 0805; C_0805_2012Metric_Pad1.15x1.40mm_HandSolder
C5, C13, C48, C50, C54, C56, C60, C62, C66, C68, C72, C74, C78, C80, C84, C86: 10nF 50V X7R 0603; C_0603_1608Metric_Pad1.05x0.95mm_HandSolder
C7, C8, C9, C10, C11, C12, C15, C16, C17, C18, C19, C20, C21, C22, C23, C24, C25, C26, C27, C28, C29, C30, C31, C32, C33, C34, C35, C36, C37, C38, C39, C40, C41, C42, C43, C44, C45: 100nF; C_0603_1608Metric_Pad1.05x0.95mm_HandSolder
F1, F2, F3, F4, F5, F6, F7, F8, F9, F10, F11, F12, F13, F14, F15, F16, F17: Polyfuse; Fuse_0603_1608Metric_Pad1.05x0.95mm_HandSolder
FB1, FB2: BLM18PG181SN1D; L_0603_1608Metric_Pad1.05x0.95mm_HandSolder
H1, H2, H3, H4: MountingHole_Pad; MountingHole_3.2mm_M3_Pad_Via
IC1, IC4, IC6, IC8, IC10, IC12, IC14, IC16: INA132UA; SOIC-8_3.9x4.9mm_P1.27mm
IC2, IC3, IC5, IC7, IC9, IC11, IC13, IC15, IC17: OPA376xxDBVR; SOT-23-5
IC18: AD5675RBRUZ; TSSOP-20_4.4x6.5mm_P0.65mm
IC19: ISO1541DR; SOIC-8_3.9x4.9mm_P1.27mm
J1: Conn_Coaxial; 73251-2200
J2, J3, J4, J5, J6, J7, J8: Conn_Coaxial; RF_SMA_RA_PCB
J9: B4B-PH-K; JST_PH_B4B-PH-K_1x04_P2.00mm_Vertical
J10, J11: JST S2B-PH-SM4; JST_PH_B2B-PH-K_1x02_P2.00mm_Vertical
JP1, JP2, JP3, JP4, JP5, JP6, JP7, JP8: SolderJumper_3_Open; SolderJumper-3_P1.3mm_Open_Pad1.0x1.5mm
L1, L2, L3, L4, L5, L6, L7, L8, L9, L10, L11, L12, L13, L14, L15, L16: MMZ2012Y152B; L_0805_2012Metric_Pad1.15x1.40mm_HandSolder
Q1, Q2, Q3, Q4, Q5, Q6, Q7, Q8: PMBT3946VPN,115; SOT-363_SC-70-6
R1, R2: 2; R_0603_1608Metric_Pad1.05x0.95mm_HandSolder
R3, R6, R9, R14, R15, R16, R19, R22, R25, R28: 1k; R_0603_1608Metric_Pad1.05x0.95mm_HandSolder
R4, R7, R10, R17, R20, R23, R26, R29: 10 0.1%; R_0805_2012Metric
R5, R8, R11, R18, R21, R24, R27, R30: 1k 0.1%; R_0805_2012Metric
R12, R33, R35, R37, R39, R41, R43, R45: 20K; R_0603_1608Metric_Pad1.05x0.95mm_HandSolder
R13, R34, R36, R38, R40, R42, R44, R46: 35.7K; R_0603_1608Metric_Pad1.05x0.95mm_HandSolder
R31, R32: 10K; R_0603_1608Metric_Pad1.05x0.95mm_HandSolder
U1, U3, U5, U7, U9, U11, U13, U15, U17: LP5907MFX-3.3; SOT-23-5
U2, U4, U6, U8, U10, U12, U14, U16: TPS7A3001; MSOP-8-1EP_3x3mm_P0.65mm_EP1.68x1.88mm

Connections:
+5V: C2.1, F2.2, F4.2, F6.2, F8.2, F10.2, F12.2, F14.2, F16.2, F17.2, FB2.1
-5V: C1.1, F1.2, F3.2, F5.2, F7.2, F9.2, F11.2, F13.2, F15.2, FB1.1
/Sheet5E20A415/Iout: IC2.3, J1.1, JP1.2
/Sheet5E20A415/Vm: C8.1, C9.2, IC1.4, IC2.2, L2.2, Q1.3
/Sheet5E20A415/Vp: C7.1, C10.1, IC1.7, IC2.5, L1.2, Q1.6
/Sheet5E20A415/sheet5E7AB32F/3.3V: C6.1, L1.1, U1.5
/Sheet5E20A415/sheet5E7AB32F/-3.3V: C13.2, C14.1, L2.1, R13.2, U2.1
/Sheet5E7753D6/Vin: C44.1, IC19.1, J9.3
/Sheet5E7753D6/scl: IC18.5, IC19.6, R32.2
/Sheet5E7753D6/sda: IC18.16, IC19.7, R31.2
/Vpower: C15.2, C42.2, C43.2, C45.1, C89.1, IC3.5, IC18.3, IC18.4, IC18.14, IC18.17, IC19.8, R31.1, R32.1, U17.5
/sheet5E6FDFF3/Iout: IC5.3, J2.1, JP2.2
/sheet5E6FDFF3/Vm: C12.1, C16.2, IC4.4, IC5.2, L4.2, Q2.3
/sheet5E6FDFF3/Vp: C11.1, C17.1, IC4.7, IC5.5, L3.2, Q2.6
/sheet5E6FDFF3/sheet5E7AB32F/3.3V: C49.1, L3.1, U3.5
/sheet5E6FDFF3/sheet5E7AB32F/-3.3V: C50.2, C51.1, L4.1, R34.2, U4.1
/sheet5E70F675/Iout: IC11.3, J5.1, JP5.2
/sheet5E70F675/Vm: C27.1, C28.2, IC10.4, IC11.2, L10.2, Q5.3
/sheet5E70F675/Vp: C26.1, C29.1, IC10.7, IC11.5, L9.2, Q5.6
/sheet5E70F675/sheet5E7AB32F/3.3V: C67.1, L9.1, U9.5
/sheet5E70F675/sheet5E7AB32F/-3.3V: C68.2, C69.1, L10.1, R40.2, U10.1
/sheet5E70F676/Iout: IC13.3, J6.1, JP6.2
/sheet5E70F676/Vm: C31.1, C32.2, IC12.4, IC13.2, L12.2, Q6.3
/sheet5E70F676/Vp: C30.1, C33.1, IC12.7, IC13.5, L11.2, Q6.6
/sheet5E70F676/sheet5E7AB32F/3.3V: C73.1, L11.1, U11.5
/sheet5E70F676/sheet5E7AB32F/-3.3V: C74.2, C75.1, L12.1, R42.2, U12.1
/sheet5E70F677/Iout: IC15.3, J7.1, JP7.2
/sheet5E70F677/Vm: C35.1, C36.2, IC14.4, IC15.2, L14.2, Q7.3
/sheet5E70F677/Vp: C34.1, C37.1, IC14.7, IC15.5, L13.2, Q7.6
/sheet5E70F677/sheet5E7AB32F/3.3V: C79.1, L13.1, U13.5
/sheet5E70F677/sheet5E7AB32F/-3.3V: C80.2, C81.1, L14.1, R44.2, U14.1
/sheet5E70F678/Iout: IC17.3, J8.1, JP8.2
/sheet5E70F678/Vm: C39.1, C40.2, IC16.4, IC17.2, L16.2, Q8.3
/sheet5E70F678/Vp: C38.1, C41.1, IC16.7, IC17.5, L15.2, Q8.6
/sheet5E70F678/sheet5E7AB32F/3.3V: C85.1, L15.1, U15.5
/sheet5E70F678/sheet5E7AB32F/-3.3V: C86.2, C87.1, L16.1, R46.2, U16.1
/sheet5E7078C0/Iout: IC7.3, J3.1, JP3.2
/sheet5E7078C0/Vm: C19.1, C20.2, IC6.4, IC7.2, L6.2, Q3.3
/sheet5E7078C0/Vp: C18.1, C21.1, IC6.7, IC7.5, L5.2, Q3.6
/sheet5E7078C0/sheet5E7AB32F/3.3V: C55.1, L5.1, U5.5
/sheet5E7078C0/sheet5E7AB32F/-3.3V: C56.2, C57.1, L6.1, R36.2, U6.1
/sheet5E7078C1/Iout: IC9.3, J4.1, JP4.2
/sheet5E7078C1/Vm: C23.1, C24.2, IC8.4, IC9.2, L8.2, Q4.3
/sheet5E7078C1/Vp: C22.1, C25.1, IC8.7, IC9.5, L7.2, Q4.6
/sheet5E7078C1/sheet5E7AB32F/3.3V: C61.1, L7.1, U7.5
/sheet5E7078C1/sheet5E7AB32F/-3.3V: C62.2, C63.1, L8.1, R38.2, U8.1
/v0: IC1.3, IC18.2
/v1: IC4.3, IC18.1
/v2: IC6.3, IC18.20
/v3: IC8.3, IC18.19
/v4: IC10.3, IC18.12
/v5: IC12.3, IC18.11
/v6: IC14.3, IC18.10
/v7: IC16.3, IC18.9
GND: C3.2, C4.2, C5.1, C6.2, C7.2, C8.2, C9.1, C10.2, C11.2, C12.2, C14.2, C15.1, C16.1, C17.2, C18.2, C19.2, C20.1, C21.2, C22.2, C23.2, C24.1, C25.2, C26.2, C27.2, C28.1, C29.2, C30.2, C31.2, C32.1, C33.2, C34.2, C35.2, C36.1, C37.2, C38.2, C39.2, C40.1, C41.2, C42.1, C43.1, C45.2, C46.2, C47.2, C48.1, C49.2, C51.2, C52.2, C53.2, C54.1, C55.2, C57.2, C58.2, C59.2, C60.1, C61.2, C63.2, C64.2, C65.2, C66.1, C67.2, C69.2, C70.2, C71.2, C72.1, C73.2, C75.2, C76.2, C77.2, C78.1, C79.2, C81.2, C82.2, C83.2, C84.1, C85.2, C87.2, C88.2, C89.2, H1.1, H2.1, H3.1, H4.1, IC3.2, IC18.6, IC18.7, IC18.8, IC18.13, IC18.15, IC19.5, J1.2, J2.2, J3.2, J4.2, J5.2, J6.2, J7.2, J8.2, J10.2, J11.1, R1.2, R2.2, R12.1, R15.1, R33.1, R35.1, R37.1, R39.1, R41.1, R43.1, R45.1, U1.2, U2.4, U2.9, U3.2, U4.4, U4.9, U5.2, U6.4, U6.9, U7.2, U8.4, U8.9, U9.2, U10.4, U10.9, U11.2, U12.4, U12.9, U13.2, U14.4, U14.9, U15.2, U16.4, U16.9, U17.2
GNDD: C44.2, IC19.4, J9.4
unnamed: C1.2, R1.1
unnamed: C2.2, R2.1
unnamed: C3.1, F1.1, U2.5, U2.8
unnamed: C4.1, F2.1, U1.1, U1.3
unnamed: C5.2, U2.6
unnamed: C13.1, R12.2, R13.1, U2.2
unnamed: C46.1, F3.1, U4.5, U4.8
unnamed: C47.1, F4.1, U3.1, U3.3
unnamed: C48.2, U4.6
unnamed: C50.1, R33.2, R34.1, U4.2
unnamed: C52.1, F5.1, U6.5, U6.8
unnamed: C53.1, F6.1, U5.1, U5.3
unnamed: C54.2, U6.6
unnamed: C56.1, R35.2, R36.1, U6.2
unnamed: C58.1, F7.1, U8.5, U8.8
unnamed: C59.1, F8.1, U7.1, U7.3
unnamed: C60.2, U8.6
unnamed: C62.1, R37.2, R38.1, U8.2
unnamed: C64.1, F9.1, U10.5, U10.8
unnamed: C65.1, F10.1, U9.1, U9.3
unnamed: C66.2, U10.6
unnamed: C68.1, R39.2, R40.1, U10.2
unnamed: C70.1, F11.1, U12.5, U12.8
unnamed: C71.1, F12.1, U11.1, U11.3
unnamed: C72.2, U12.6
unnamed: C74.1, R41.2, R42.1, U12.2
unnamed: C76.1, F13.1, U14.5, U14.8
unnamed: C77.1, F14.1, U13.1, U13.3
unnamed: C78.2, U14.6
unnamed: C80.1, R43.2, R44.1, U14.2
unnamed: C82.1, F15.1, U16.5, U16.8
unnamed: C83.1, F16.1, U15.1, U15.3
unnamed: C84.2, U16.6
unnamed: C86.1, R45.2, R46.1, U16.2
unnamed: C88.1, F17.1, U17.1, U17.3
unnamed: FB1.2, J11.2
unnamed: FB2.2, J10.1
unnamed: IC1.1, IC2.1, IC2.4
unnamed: IC1.5, Q1.1, Q1.4, R3.1, R4.1, R5.1
unnamed: IC1.6, Q1.2, Q1.5, R3.2
unnamed: IC3.3, R14.1, R15.2
unnamed: IC4.1, IC5.1, IC5.4
unnamed: IC4.5, Q2.1, Q2.4, R6.1, R7.1, R8.1
unnamed: IC4.6, Q2.2, Q2.5, R6.2
unnamed: IC6.1, IC7.1, IC7.4
unnamed: IC6.5, Q3.1, Q3.4, R9.1, R10.1, R11.1
unnamed: IC6.6, Q3.2, Q3.5, R9.2
unnamed: IC8.1, IC9.1, IC9.4
unnamed: IC8.5, Q4.1, Q4.4, R16.1, R17.1, R18.1
unnamed: IC8.6, Q4.2, Q4.5, R16.2
unnamed: IC10.1, IC11.1, IC11.4
unnamed: IC10.5, Q5.1, Q5.4, R19.1, R20.1, R21.1
unnamed: IC10.6, Q5.2, Q5.5, R19.2
unnamed: IC12.1, IC13.1, IC13.4
unnamed: IC12.5, Q6.1, Q6.4, R22.1, R23.1, R24.1
unnamed: IC12.6, Q6.2, Q6.5, R22.2
unnamed: IC14.1, IC15.1, IC15.4
unnamed: IC14.5, Q7.1, Q7.4, R25.1, R26.1, R27.1
unnamed: IC14.6, Q7.2, Q7.5, R25.2
unnamed: IC16.1, IC17.1, IC17.4
unnamed: IC16.5, Q8.1, Q8.4, R28.1, R29.1, R30.1
unnamed: IC16.6, Q8.2, Q8.5, R28.2
unnamed: IC19.2, J9.2
unnamed: IC19.3, J9.1
unnamed: JP1.1, R4.2
unnamed: JP1.3, R5.2
unnamed: JP2.1, R7.2
unnamed: JP2.3, R8.2
unnamed: JP3.1, R10.2
unnamed: JP3.3, R11.2
unnamed: JP4.1, R17.2
unnamed: JP4.3, R18.2
unnamed: JP5.1, R20.2
unnamed: JP5.3, R21.2
unnamed: JP6.1, R23.2
unnamed: JP6.3, R24.2
unnamed: JP7.1, R26.2
unnamed: JP7.3, R27.2
unnamed: JP8.1, R29.2
unnamed: JP8.3, R30.2
Vref: IC18.18, R14.2
offset: IC1.2, IC3.1, IC3.4, IC4.2, IC6.2, IC8.2, IC10.2, IC12.2, IC14.2, IC16.2

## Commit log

2020-12-09 Add all hardware cad files
    [1455L1201.stp, 191-009-113.STEP, 4600 QTPy.step, B2B-PH-SM4-TB.STEP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]
2020-12-09 Add assembly instructions
2020-12-09 Upddate assembly instructions
2021-01-21 t add pmos boaard
    [back_panel.sch, coax_ch.sch, front_panel.kicad_pcb, front_panel.sch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]
2021-01-24 Update to pmosboard
    [coax_ch.sch, front_panel.kicad_pcb, pmos_board.kicad_pcb, pmos_board.sch]
2021-01-24 add power (inside 8ch_v5_nosma) add back panel add front panel
    [182-009-213.STEP, 191-009-113.STEP, 4600 QTPy.step, 8ch_v5_nosma-B_Cu.gbl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]
2021-01-24 fix problem with front-panel... elminate thermals
    [front_panel.kicad_pcb]
2021-01-24 Add gerbers for front_v3
    [front_panel-B_Cu.gbr, front_panel-B_Mask.gbr, front_panel-B_Paste.gbr, front_panel-B_SilkS.gbr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]
2021-02-05 update back_v3
    [8ch_v5_nosma.sch, back_v2-B_SilkS.gbr, back_v2-F_Cu.gbr, back_v2-F_Paste.gbr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]
2021-02-15 Add github actions
    [front_panel.kicad_pcb, power_cui.kicad_pcb, power_cui.step]
2021-02-15 rearrange folders
    [182-009-213.STEP, 191-009-113.STEP, 4600 QTPy.step, B2B-PH-SM4-TB.STEP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]
